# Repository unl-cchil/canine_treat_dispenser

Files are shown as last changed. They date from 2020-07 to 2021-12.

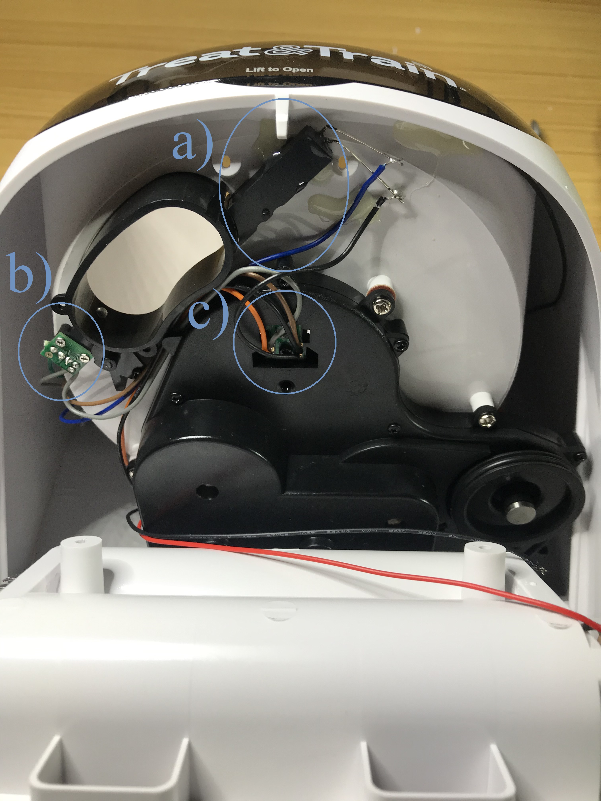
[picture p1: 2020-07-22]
documentation/figures/figure1.jpg

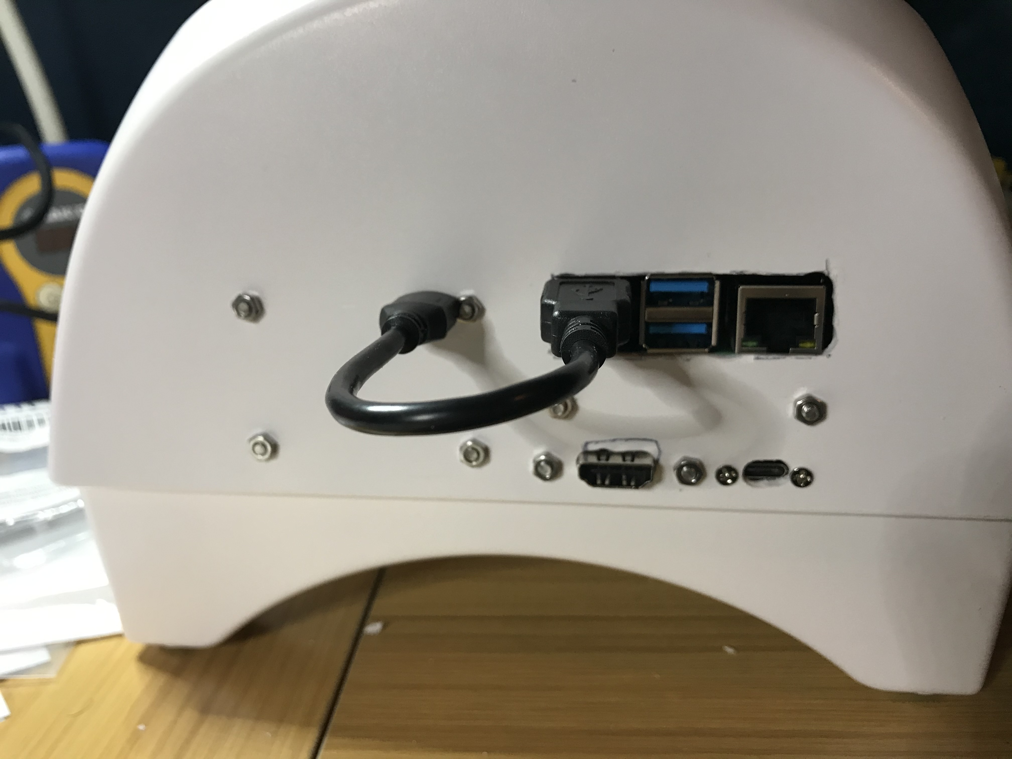
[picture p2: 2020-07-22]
documentation/figures/figure6.jpg

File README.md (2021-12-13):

# Computer-controlled dog treat dispenser

**This project retrofits an existing off-the-shelf dog treat dispenser with new electronics that allow it to be controlled by a computer.**

### Overview

When performing canine operant conditioning studies, the delivery of the reward can be a limiting factor of the study. While there are a few commercially available options for automatically delivering rewards, they generally require manual input, such as using a remote control, in accordance with the experiment script. This means that human reaction times and transmission distances can cause interruptions to the flow of the experiment. The potential for development of non-supervised conditioning studies is limited by this same factor. To remedy this, we retrofitted an off-the-shelf treat dispenser with new electronics that allow it to be remotely controllable as well as act as an experiment computation, data storage, and networking center. We present a fully integrated dispenser driver board with a complementary Raspberry Pi. With rather simple modifications, the commercial treat dispenser can be modified into a computer-controlled dispenser for canine cognition experiments or for other forms of canine training or games.

[Demonstration video](https://www.youtube.com/watch?v=veKvqE5ipu4)

### License

The software and hardware designs are available under a [Creative Commons Attribution-ShareAlike 4.0 International Public License (CC BY-SA 4.0)](https://creativecommons.org/licenses/by-sa/4.0/). You are free to:

* Share — copy and redistribute the material in any medium or format
* Adapt — remix, transform, and build upon the material for any purpose, even commercially.

Under the following terms:

* Attribution — You must give appropriate credit, provide a link to the license, and indicate if changes were made. You may do so in any reasonable manner, but not in any way that suggests the licensor endorses you or your use.
* ShareAlike — If you remix, transform, or build upon the material, you must distribute your contributions under the same license as the original.

### Contact

This project was conducted by the [Canine Cognition and Human Interaction Lab](https://dogcog.unl.edu) and funded by the [National Science Foundation](https://nsf.gov). For questions, please contact the developer Walker Arce (warce@unomaha.edu) or the principal investigator Jeffrey R. Stevens (jeffrey.r.stevens@gmail.com).

### Citation
Arce, W., & Stevens, J. R. (2020). Developing a computer-controlled treat dispenser for canine operant conditioning. _Journal of Open Hardware_, 4(1), 6. https://doi.org/10.5334/joh.27

### Project Mentions
[Hackaday](https://hackaday.com/2020/10/31/using-open-source-to-train-your-dog/)

[Open Neuroscience](https://open-neuroscience.com/post/computer_controlled_dog_treat_dispenser/)

### Dataset Metadata
The following table is necessary for this dataset to be indexed by search
engines such as <a href="https://g.co/datasetsearch">Google Dataset Search</a>.
<div itemscope itemtype="http://schema.org/Dataset">
<table>
<tr>
<th>property</th>
<th>value</th>
</tr>
<tr>
<td>name</td>
<td><code itemprop="name">Computer-controlled dog treat dispenser reliability testing dataset</code></td>
</tr>
<tr>
<td>description</td>
<td><code itemprop="description">The dataset from the paper [Developing a computer-controlled treat dispenser for canine operant conditioning](https://doi.org/10.5334/joh.27). We tested two treat dispensers 100 times each with 10 tests of increasing dispensing targets from 1 to 10 treats. Each row of the data file gives the expected and actual number of treats dispensed for a single trial.</code></td>
</tr>
</tr>
<tr>
<td>url</td>
<td><code itemprop="url">https://github.com/unl-cchil/canine_treat_dispenser</code></td>
</tr>
<tr>
<td>sameAs</td>
<td><code itemprop="sameAs">https://github.com/unl-cchil/canine_treat_dispenser</code></td>
</tr>
<tr>
<td>citation</td>
<td><code itemprop="citation">https://doi.org/10.5334/joh.27</code></td>
</tr>
<tr>
<td>license</td>
<td>
<div itemscope itemtype="http://schema.org/CreativeWork" itemprop="license">
<table>
<tr>
<th>property</th>
<th>value</th>
</tr>
<tr>
<td>name</td>
<td><code itemprop="name">CC BY-SA 4.0</code></td>
</tr>
<tr>
<td>url</td>
<td><code itemprop="url">https://creativecommons.org/licenses/by-sa/4.0/</code></td>
</tr>
</table>
</div>
</td>
</tr>
</table>
</div>

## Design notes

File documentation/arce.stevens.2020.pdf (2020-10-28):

## HARDWARE METAPAPER

# Developing a Computer-Controlled Treat Dispenser for Canine Operant Conditioning

## Walker Arce*

## and Jeffrey R. Stevens†

When performing canine operant conditioning studies, the delivery of the reward can be a limiting factor of the study. While there are a few commercially available options for automatically delivering rewards, they generally require manual input, such as using a remote control, in accordance with the experiment script. This means that human reaction times and transmission distances can cause interruptions to the flow of the experiment. The potential for development of non-supervised conditioning studies is limited by this same factor. To remedy this, we retrofitted an off-the-shelf treat dispenser with new electronics that allow it to be remotely controllable as well as act as an experiment computation, data storage, and networking center. We present a fully integrated dispenser driver board with a complementary Raspberry Pi. With rather simple modifications, the commercial treat dispenser can be modified into a computer-controlled dispenser for canine cognition experiments or for other forms of canine training or games.

Keywords: Canine; computer-controlled dispenser; operant conditioning; retrofitted dispenser
Funding Statement: This research was supported by a National Science Foundation grant to JRS (SES-1658837), including a Research Experiences for Undergraduates (REU) stipend to WA, and by a University of Nebraska-Lincoln Research Council Grant-in-Aid to JRS.

### Metadata Overview

Main design files: https://github.com/unl-cchil/canine_
treat_dispenser. (https://github.com/unl-cchil/canine_treat_dispenser)
Target group: Scientists in canine cognition.
Skills required: Desktop 3D printing, surface mount electronics assembly.
Replication: No builds known to the authors so far.
See section “Build Details” for more detail.

### (1) Overview Introduction

Operant conditioning is a critical tool used to train pet dogs (McKinley and Young 2003). In particular, positive reinforcement involves providing a reward in the presence of a behavior to increase the expression of that behavior (McKinley and Young 2003). Clicker training is a classic example of employing operant conditioning in dogs, where a command is given and, if the dog expresses the correct behavior (or an approximation of that behavior), the dog handler presses the clicker and follows up with a food treat or other reward. These forms of operant conditioning are often used in training obedience and in reducing problem behaviors (Reisner 2016).
Operant conditioning is also used by researchers interested in studying aspects of dog cognition (McKinley and Young 2003). Clicker training, however, is often not ideal for these studies because the clicker and food dispensing must be implemented by a person, which may distract the dog from the cognitive task. For that reason, studies of dog cognition often use automated treat dispensers that are triggered by the researchers, sometimes with remote controls. For example, canine cognition can be tested by dispensing a treat when the animal subject touches a visual indicator on a screen (see demonstration video at https://www.youtube.com/watch?v=veKvqE5ipu4). This allows researchers to present a range of different stimuli to the dogs, record their responses, and reinforce the responses with food treats.
The PetSafe Treat & Train Manners Minder Remote Reward Dog Trainer (PetSafe 2020) is a commercial treat dispenser for training pet dogs at home using operant conditioning techniques. A user can dispense treats using a radio frequency (RF) remote control. The Treat & Train (PetSafe 2020) is a commonly used treat dispenser for canine operant conditioning, and it is generally controlled using its RF remote, dispensing a single treat per button press (Hiby et al. 2004, Yin et al. 2008, Hardin et al. 2015, Protopopova et al. 2016, Majikes 2017, Wallis et al. 2017, Edwards 2019). However, the inconsistencies in the human operating the remote, as well as the remote’s

Arce, W and Stevens, JR. 2020. Developing a Computer-Controlled Treat Dispenser for Canine Operant Conditioning. Journal of Open Hardware, 4(1): 6, pp. 1–10. DOI: https://doi.org/10.5334/joh.27

* Department of Electrical and Computer Engineering, University of Nebraska-Lincoln, US
† Department of Psychology, Center for Brain, Biology and Behavior, University of Nebraska-Lincoln, US
Corresponding author: Jeffrey R. Stevens (jeffrey.r.stevens@gmail.com)

Art. 6, page 2 of 10 | Arce and Stevens: Developing a Computer-Controlled Treat Dispenser for Canine Operant Conditioning

range, can limit the effectiveness of the treat dispenser.
There have been instances of these dispensers being retrofitted to automatically dispense treats, but there have not been any published examples of the method to do so (Wallis et al. 2017). There have, however, been published builds of food-dispensing devices for other species, such as fruit flies (Wayland et al. 2018).
Our aim here is to describe the construction, operation, and reliability of a dispenser that not only is directly controlled by a computer (rather than a remote control) but is a self-contained experimenting system when a Raspberry Pi is integrated into the Treat & Train. To do this, we created a custom-printed circuit board to drive the dispenser. We integrated a Raspberry Pi 4 single-board computer (Raspberry Pi Foundation 2020) and our custom-printed circuit board into the existing Treat & Train (PetSafe 2020) dispenser to create a computer-controlled adaptation of this commonly used device. Our creation allows stimulus generation using common experiment generation software such as PsychoPy (Peirce 2007), controls reward delivery, and performs data collection and transfer in a single, self-contained unit. This paper outlines the methods performed to retrofit the Treat & Train dispenser, the hardware and software designed, and the results of reliability testing in the dispensing of treats. All documentation and firmware are available at https://github.com/unl-cchil/canine_treat_dispenser. (https://github.com/unl-cchil/canine_treat_dispenser)

### Overall Implementation and Design

Treat & Train System
The Treat & Train dispenser consists of a rotating wheel with cutouts that allow treats to fall from the treat storage area to a feeding receptacle. A motor rotates the wheel and a photo interrupter sensor detects whether a treat was dispensed (Figure 1). This means that applying a constant current source to an infrared (IR) transmitter (LED) and an IR receiver and monitoring the output of the receiver will indicate if there is an object blocking the LED. In the case of our system, this would indicate that a treat has been dispensed, which is the output we are trying to detect. Additionally, there is a photo interrupter in the base of the dispensing wheel that can detect the movement of the wheel.
To power the IR LED, we inserted a current-limiting resistor in series with the LED power supply. On the negative end we wanted to monitor the output voltage, which should be proportional to the amount of IR light interacting with it. To do this, we placed a resistor divider of sufficiently high resistance to measure the output voltage. This allows the circuit to act as a voltmeter and gives us sufficient resolution to detect treats crossing the IR beam. The Treat & Train has a brushed DC motor on-board that drives a gear and pulley system to the main dispensing wheel. The stock dispenser drives this motor at 6 VDC in one direction. For our purposes, we allowed more flexibility by

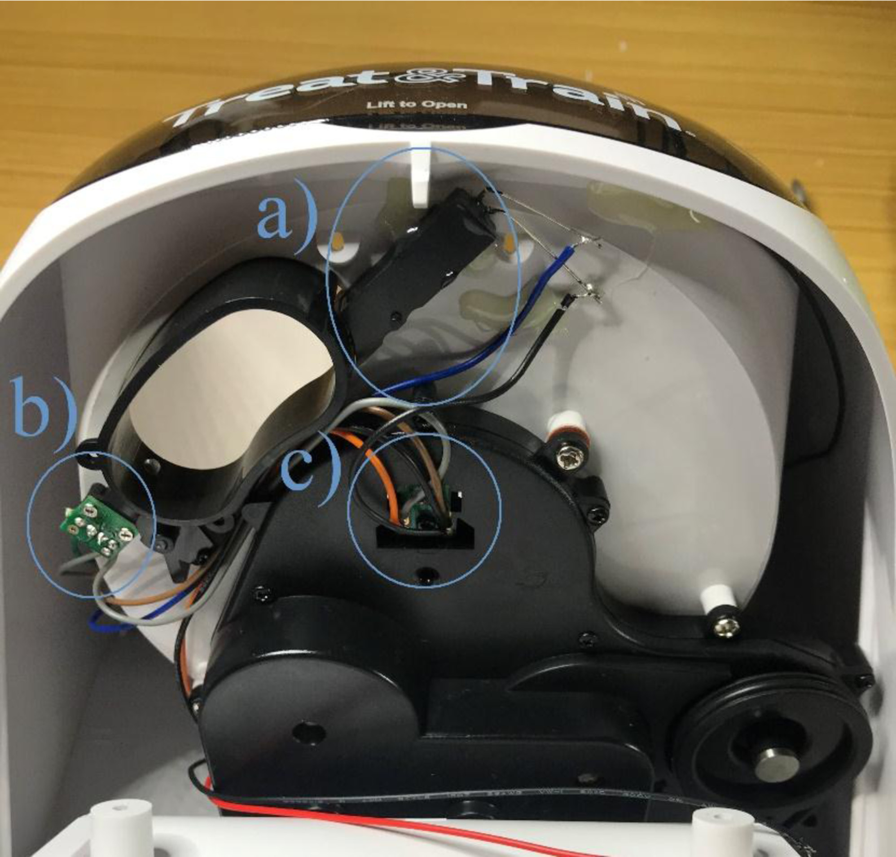
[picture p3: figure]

Figure 1: Location of the two IR transmitter-receiver pairs, where (a) is the treat IR receiver, (b) is the treat IR LED—so
(a) and (b) constitute a single photo interrupter—and (c) is the wheel photo interrupter, with both parts integrated into a single package.

Arce and Stevens: Developing a Computer-Controlled Treat Dispenser for Canine Operant Conditioning | Art. 6, page 3 of 10

using a motor driver chip to drive the motor and control
its speed. To drive a 6 VDC motor from a USB power supply, which is set to 5 VDC, we needed to boost the voltage. To allow some excess capacity/voltage for future implementations, we designed a boost regulator with an output voltage of 12 VDC.

Hardware Development
We developed a simple driver board with a USB interface, microcontroller, power stage, motor interface, and an interface for the Treat & Train sensors. We used a microcontroller to drive these circuits, an ARM Cortex-M0+, which is supported by the Arduino IDE for easy programmability and customization. This system was then paired with a Raspberry Pi 4 to create a self-contained dispenser. Additionally, we combined this system with a television display and a USB infrared touchscreen device that is used as mouse input. The result is a complete operant system in which stimuli are presented on the television display, responses are recorded by the touchscreen, and treats are automatically dispensed based on the responses (see demonstration video at https://www.youtube.com/watch?v=veKvqE5ipu4). (https://www.youtube.com/watch?v=veKvqE5ipu4) The connection diagram for this is shown in Figure 2.

Next, we designed the interfaces to the Treat & Train main board, which had all of its internal connections severed to be interfaced to our circuits. The first circuit is the digital interface for the RF remote ‘click’ signal that dispenses treats. This is triggered by connecting the positive motor output of the Treat & Train main board to a transistor circuit that would energize when the main board tries to drive the motor. This retains RF remote control functionality. The second circuit is the analog voltage sensing resistor divider, for which we used 1 MΩ resistors to keep the current drawn low. These are shown in Figure 3.
For the custom board, we used an ARM Cortex-M0+ microcontroller (ATSAMD21E from Microchip), with a TB6612 motor driver (Figure 4). The USB voltage was regulated to 3.3 VDC using an AP2112k low dropout regulator and the 12 VDC for the motor was generated using an LMR6201 1.6 MHz step-up converter with a 1.4 A switch. Finally, the right-angle USB connector was mounted such that it would be exposed out of the back wall of the Treat & Train.
This board was designed to work with the “Sparkfun Qwiic Micro” bootloader (Microsoft 2019) that is available through the Boards Manager in the Arduino IDE. Reference this firmware when determining what the

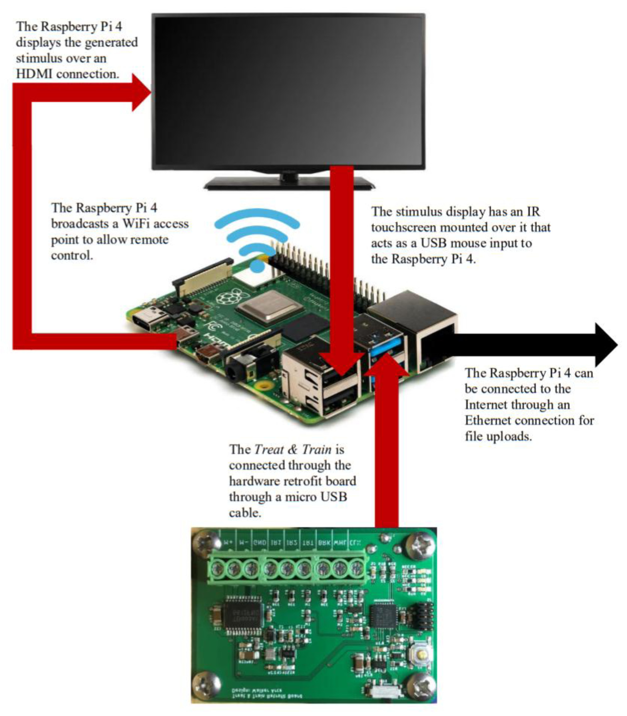
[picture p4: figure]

Figure 2: Connection diagram for the developed hardware.

Art. 6, page 4 of 10 | Arce and Stevens: Developing a Computer-Controlled Treat Dispenser for Canine Operant Conditioning

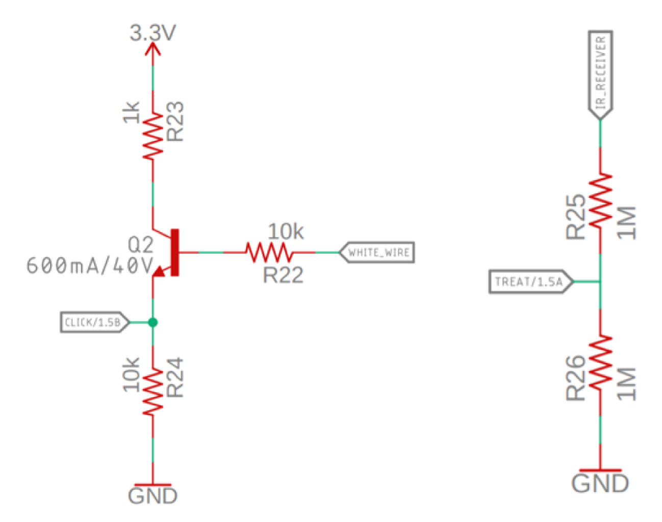
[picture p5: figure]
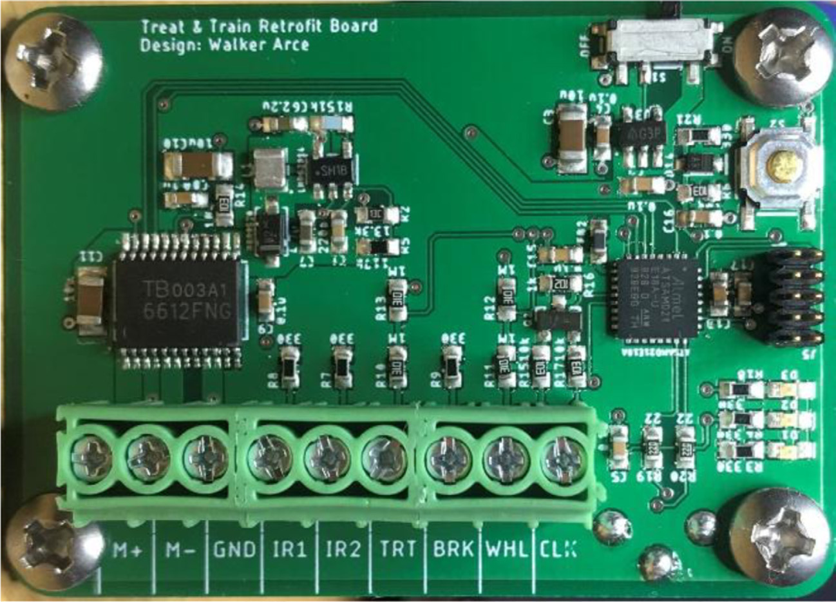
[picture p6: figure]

Arduino pin names refer to if using this firmware with another processor. The pins that are broken out on the screw terminals are shown in Table 1 and are valid for firmware version 0.4.
The internal connections from the microcontroller to the motor driver are specified in Table 2.

Software Development
Our implementation will have two sets of software: one set that runs on the microcontroller and another that runs on a host computer, in this case the Raspberry Pi. We composed the first set in the Arduino IDE 1.8.12 (Arduino 2020) using an open-source bootloader and the second using Python (Python Software Foundation 2019), which allows for cross-platform compatibility and testing.
The firmware for the current implementations is at version 0.4 and was designed using the Arduino IDE 1.8.12 (Arduino 2020). The firmware running on the custom-printed circuit board operates using a defined USB protocol driven by byte codes. This can be easily expanded upon by adding cases to the switch statement for the command byte (Table 3). A response of 0x00 indicates the command successfully executed and a response of 0x01 indicates the command failed. Commands are processed in the order they are received.

Figure 3: (Left) Transistor to detect the RF remote being activated, (Right) resistor divider circuit to read the IR receiver output voltage. Note: “WHITE WIRE” is the hardware connection to the RF receiver; “CLICK” is the output signal for the RF receiver; “TREAT” is the voltage reading from the output of the IR receiver.

Figure 4: Custom printed circuit board.

Arce and Stevens: Developing a Computer-Controlled Treat Dispenser for Canine Operant Conditioning | Art. 6, page 5 of 10

There are a few pre-defined commands for this version of the firmware, one of which is not accessible through USB input (Table 4).
On the Pi, a Python class was implemented to send the above commands over a USB serial link to the driver board. This class was used with PsychoPy in the experiment script.

Dispenser Development
To run entire experimental setups, perform the visualization of input stimulus, control stimulus devices, and log generated data, we integrated a Raspberry Pi 4 (Raspberry Pi Foundation 2020) single-board computer running the default Raspberry Pi OS (Raspberry Pi Foundation 2020). This allowed us to achieve three goals:
1 | Wireless Access Point
| – The Raspberry Pi 4 can host its own WiFi access
| point, which allows the experimenter to connect
| to the Pi and run experiments, download results,
| and interact with the main system.
2 | Decoupled Interfaces
| – The experimenter’s screen and the screen used
| by the canine are separate and require no extra
| hardware to achieve. By connecting to the Pi us-
| ing SSH (Secure Shell), the command line can

be exposed to run the experiments. The canine screen can be connected to the HDMI0 of the Pi and the SSH session can be started over a wireless connection.
3 | Simple Setup
| – The system is expected to be easy to setup and
| maintain. We can use robust packages such as pi-
| ap (Houlahan 2019) and SD card backups to eas-
| ily restore the dispenser and get new dispensers
| up and running.

Achieving the above three criteria allows for a launching point towards more complex and integrated solutions for automated reward delivery and data logging.
The final dispenser with the new electronics and functionality had its connectors exposed on the back wall of the dispenser. The connections include the USB connector to the retrofitted control board, the Raspberry Pi 4 USB connectors, an HDMI port, Ethernet jack, and the USB-C power supply input port. This allows the Raspberry Pi 4 to display stimuli on a screen connected to the HDMI port and accept mouse inputs from an IR touchscreen adapter through on of the Pi USB ports. The Pi can also be network connected through the Ethernet jack. A short USB cable from the Pi provides power and serial communications

Table 1: Custom board pin descriptions and functions, applicable to firmware version 0.4.

Pin Name Arduino Pin Function Description
M+ | N/A | Output | Connected to positive motor pin
M- | N/A | Output | Connected to negative motor pin
GND | N/A | Input | Common ground pin
IR1 | N/A | Output | 3.3V power supply for IR LEDs, current limited to 5mA
IR2 | N/A | Output | 3.3V power supply for IR LEDs, current limited to 5mA
TRT | A1 | Input | IR receiver sensor from treat sensor
BRK | N/A | Output | 3.3V power supply for photointerrupter sensors, current limited to 1mA
WHL | A3 | Input | IR receiver sensor output from wheel sensor
CLK | D8 | Input | RF remote input for ‘Dispense’ button

Table 2: Arduino pin names and descriptions.

Pin Name Arduino Pin Description
AIN1 | D7 | First input for motor driver, invert from other input to drive motor in one direction or the other.
AIN2 | D6 | Second input for motor driver, invert from other input to drive motor in one direction or the other.
PWMA | D3 | PWM input that controls the speed of the motor

Table 3: USB protocol byte descriptions.

| Name | Value | Function
Start Byte | 67 (Dec), 0x43, ‘C’ Signals the system to start listening for input
Command Byte 1 byte | Command defined below
| Data Byte | 1 byte | Defined based on commands
End Byte | 69 (Dec), 0x45, ‘E’ Signals the end of the current command

Art. 6, page 6 of 10 | Arce and Stevens: Developing a Computer-Controlled Treat Dispenser for Canine Operant Conditioning

to the driver board. This USB cable can be removed from the Pi, and the dispenser can be connected directly to a standard PC—bypassing the Raspberry Pi—to operate the retrofitted dispenser. This is shown in Figure 5.
The dispenser, when turned on, creates a WiFi access point called “operant-canine-xx”, with “xx” being the dispenser number, i.e. “01” with a local address of
pi@192.168.0.1 and the password raspberry,
which are the default values in the pi-ap configuration. This can be modified in the pi-ap software. By connecting to this AP, the Raspberry Pi can be accessed through SSH using a program such as PuTTY (Tatham 2020).
To use the RF remote to trigger the system, the Treat & Train main board must first be turned on before powering on the retrofitted board. If the Treat & Train is turned on after the retrofitted board, the ‘CLK’ signal will go high, as it is controlled through a transistor that is not turned off when the board is first powered on. Do not use anything other than a computer USB port for powering the system. The retrofitted board does not power the Treat & Train main board, so it will still require four D cell batteries to operate with backwards compatibility. This should be fixed in the next revision and the RF receiver should be powered by the custom printed circuit board.

### (2) Quality Control Safety

Operators of this dispenser should be aware of four hazards:

- Finger pinches.
- Electric shock.
- Burns when assembling electronics.
- Damage to Treat & Train.

Finger Pinches
The dispenser wheel turns continuously from a DC motor to dispense treats through an eyelet that, if not careful, can cause the user’s finger to be pinched when trying to fix a jam.

Electric Shock
The powering of electronics using an external power source, such as when testing a newly developed circuit, can cause electric shocks if not careful. Work tables should be placed where there is no risk of splashing water. All cables used to connect sensors and power should be inspected for damage and replaced if necessary.

Burns during Assembly
The assembly of the described electronics includes the use of soldering irons and hot air rework tools. These tools use high temperatures to melt solder and pose a risk of burning when used improperly. Ensure that the user’s manuals are read and adhered to when using new tools.

Damage to Treat & Train
When retrofitting an off-the-shelf device, there is always a risk of damaging or destroying the on-board electronics. Before applying power to any on-board sensors, double check your power supply and connections to prevent short circuits and over-voltage/over-current situations.

### General Testing

Considering one line of canine behavior and psychology research includes the design of numerical preference studies (Ward 2007, Baker 2012, Miletto Petrazzini et al. 2020), we tested the dispenser’s accuracy of dispensing treats. This gives benchmarks that allow for future work that may be needed to meet specific performance deficits that exist in the current setup and for the dispenser to be adapted to new types of studies.
For this testing, we wanted to measure the failure rate of the dispensing commands, meaning the amount over or under that it dispenses from the target amount. To do this, we performed a total of 100 tests split into 10 tests of increasing dispensing targets from 1 to 10 treats, in steps of one treat. These tests were performed using two of the described dispensers, which were filled up to the “1 cup” line with Pet Botanics Training Reward treats, which are cylindrical treats that fit through the larger dispenser wheel. Reliability data are available at https://github.com/unl-cchil/canine_treat_dispenser. (https://github.com/unl-cchil/canine_treat_dispenser)
The results for this testing are shown in Tables 5 and 6. We tracked the mean number of treats dispensed for each dispenser tested (columns Actual One and Two), the number of treats dispensed that were over or under the expected number in each set of tests (columns Errors One

Table 4: USB commands that follow Table 3 protocol.

Command | Command Byte Data | Function
Dispense | ‘D’ | ‘0’–’9’ Command to dispense up to 9 treats.
Print | ‘P’ | ‘0’ | Prints current value of sensors, data field is set to zero in ASCII (‘0’).
Update RF | ‘B’ | ‘0’–’9’ Updates the number of treats that will be dispensed when using the RF remote.
Dispense | ‘A’ | 0–255 Command to dispense up to 255 treats.
Motor Update ‘M’ | 0–255 Updates the motor speed used when operating the dispenser in any mode.
| | | Default: 127
Wheel Test | ‘F’ | ‘0’ | Performs the wheel test routine to verify operation of the firmware and sensors.
RF Dispense | N/A | N/A | By clicking the ‘Dispense’ button on the RF remote, the system will dispense the defined number of treats. Default: 1 treat

Arce and Stevens: Developing a Computer-Controlled Treat Dispenser for Canine Operant Conditioning | Art. 6, page 7 of 10

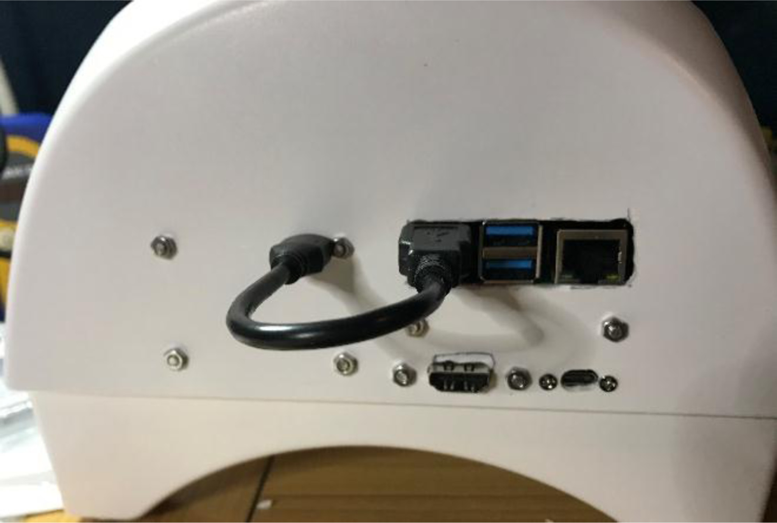
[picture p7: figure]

and Two), the mean number of treats dispensed averaged across the two dispensers (column Mean Actual), and the mean number of failures between the two dispensers (Mean Error).
Each dispensing command has a potential error rate of 32% in the first dispenser and 22% in the second dispenser. This means that over- or under-dispensing occurs roughly every third and fourth event, respectively.

### (3) Application Use Case(s)

The modified Treat & Train was designed to be used in canine cognition studies and be controlled by a script to perform the reward dispensing in response to input from the canine subject. This described tools can also reasonably act as a platform for new dispenser development, which can be specifically designed for canine cognition research, such as precise dispensers.

Figure 5: Peripheral interface for the dispenser.

Table 6: Results of the reliability testing.

Dispense | Actual One Actual Two Errors One Errors Two Mean Actual Mean Error
1 | 1.10 | 1.00 | 1 | 0 | 1.05 | 0.50
2 | 2.40 | 2.20 | 4 | 2 | 2.30 | 3.00
3 | 3.40 | 3.30 | 4 | 3 | 3.35 | 3.50
4 | 4.10 | 4.00 | 1 | 0 | 4.05 | 0.50
5 | 5.20 | 5.30 | 2 | 3 | 5.25 | 2.50
6 | 6.40 | 6.50 | 4 | 5 | 6.45 | 4.50
7 | 7.60 | 7.10 | 6 | 1 | 7.35 | 3.50
8 | 8.50 | 8.60 | 4 | 4 | 8.55 | 4.00
9 | 9.50 | 9.20 | 4 | 2 | 9.35 | 3.00
10 | 10.00 | 10.20 | 2 | 2 | 10.10 | 2.00
Mean Error | | | 32.0% | 22.0% | | 27.0%

Table 5: Results of the treat dispensing trials.

Total Treats
Dispensed

Correct Number
Dispensed

Over-Dispensing Under-Dispensing

First Dispenser | 100 | 68 | 31 | 1
Second Dispenser | 100 | 78 | 22 | 0

Art. 6, page 8 of 10 | Arce and Stevens: Developing a Computer-Controlled Treat Dispenser for Canine Operant Conditioning

Further, this may be used by dog owners who are training their dogs for particular tasks or who would like to
develop games for their dogs to play. Existing commercial dispensers such as PupPod (PupPod 2020) allow for inputs from embedded sensors in toys. But they do not connect to touchscreens, which could provide rich possibilities for games. Our dispenser allows a wider range of potential stimuli to be presented to and responses to be recorded from dogs to trigger a reward.
Since the Raspberry Pi 4 has an on-board Bluetooth modem, this allows for integration of other custom devices such as inertial measurement units (IMUs), which measure its own movement in terms of acceleration in the X, Y, and Z axes, to allow a canine’s position and movement to control treat dispensing (Protopopova et al. 2016, Majikes 2017). Additionally, the sound output of the Pi can allow for sound triggers in the operant conditioning protocol (Protopopova et al. 2016, Edwards 2019).

### Reuse Potential and Adaptability

With the included Raspberry Pi 4, custom sensors can be easily integrated through Python scripting to trigger the dispensing command. The developed Python class and custom hardware allow for control of other dispensers, such as for bird or rat pellets. Common off-the-shelf dispensers use a single motor to dispense sequential treats, in a similar fashion as the Treat & Train; due to this the presented hardware would work on those systems.

### (4) Build Details Availability of Materials and Methods

Building the custom hardware requires the use of a soldering iron, hot air rework gun, reflow oven, precise tweezers, and a vise. All the parts for this part of the build are available from DigiKey and a PCB manufacturer.
The retrofitting operation requires a 3D printed Raspberry Pi mount, a Dremel for exposing ports on the Treat & Train, and various M3 screws. Additionally, the extra parts, such as HDMI cables and ports, for the Raspberry Pi 4 are available from Amazon.

### Ease of Build

The parts used in the build are readily available from online vendors such as Adafruit and DigiKey. The custom version requires the operation of more advanced tools such as a hot air gun or reflow oven, pick and place or precise tweezers, and solder paste and flux. We estimate the build can be performed in around eight hours with sufficient planning and experience from start to finish for the DIY version.

### Operating Software and Peripherals

For the custom hardware, Arduino IDE 1.8.12 was used as the development environment. For the Raspberry Pi 4, the Raspberry Pi OS was used as well as pyserial (version 3.4), PsychoPy (version 3.2.4), and pi-ap (version 1.10.02).

### Dependencies

This build requires the use of pi-ap (Houlahan 2019), Raspberry Pi OS (Raspberry Pi Foundation 2020), and

Arduino IDE (Arduino 2020). The driving software to send commands over the USB port is written in Python 3.7.6 (Python Software Foundation 2019).

### Hardware Documentation and File Location

Name: GitHub
Persistent identifier: https://github.com/unl-cchil/canine_treat_dispenser (https://github.com/unl-cchil/canine_treat_dispenser)
Licence: Creative Commons CC-BY-SA, 4.0 Publisher: Jeffrey R. Stevens
Date published: 29/07/2020
Software is stored together with the hardware files, in the same repository.
Licence: Creative Commons CC-BY-SA, 4.0
Date published: 29/07/2020

### (5) Discussion Conclusions

This study presented a method by which a common, offthe-shelf, canine treat dispenser can be modified to conduct operant conditioning studies using a computer interface. Using the presented version, the common Arduino platform was used to interface to the onboard photo interrupters and control the dispensing motor, achieving the same functionality as the original dispenser but controlled by a computer. This computer, a Raspberry Pi 4, was integrated to the new hardware to run a Linux distribution and operate the generation of stimulus through PsychoPy (Peirce 2007). In adding this central computing platform, all results from the experiments can be centrally stored and easily accessed for future processing and reporting.
By making this dispenser DIY and open-source, researchers may expand on the work and include new trigger methods ranging from sound to ultrasonic distance sensing. By having a single-board computer housed within the dispenser, experiment control software can be generated and run by using the tested and supported PsychoPy Python package (Peirce 2007). Additionally, this setup allows for cross-platform development, meaning that any software already generated using the PsychoPy package is supported. The inclusion of the Raspberry Pi 4 also makes the entire setup mobile, so experiments can be conducted outside of the laboratory.
The demonstrated computer-controlled dispenser can be readily used and assembled with minimal skill and can act as a jumping off point for automated canine operant conditioning studies. Since automated reward dispenser are difficult to build from scratch, our proposed modifications of the Treat & Train would allow for researchers to integrate an automated dispenser into their studies (Hardin et al. 2015, Protopopova et al. 2016, Majikes 2017, Wallis et al. 2017, Robinson et al. 2020). Additionally, since the use of positive reinforcement training has been shown to indicate an increased level of obedience, our dispenser can be used in at-home situations for canine training exercises (Hiby et al. 2004).
The average error rate between the two dispensers is 27%, which is an error every fourth dispensing command. These errors often happen when two treats stack in the

Arce and Stevens: Developing a Computer-Controlled Treat Dispenser for Canine Operant Conditioning | Art. 6, page 9 of 10

output hole and, when it dispenses, both fall through,
leading to dispensing one extra treat. If, for instance,
a circular or thicker treat were used, this issue could be mitigated. Alternatively, modifying the dispensing wheel to limit the number of treats grabbed could also help. As for situations where the treat would jam the movement of the wheel, the force of the turning wheel would cut the treat in half, as the treats used in testing were pliable enough to allow for this. This resolved the issue when it presented itself, but this may not be the case for all treat types.
For studies in which precise treat dispensing is not required, our work allows researchers to relatively inexpensively adapt an off-the-shelf product into a treat dispenser that can be controlled either by a personal computer or a Raspberry Pi, thus facilitating operant conditioning studies in dogs.

### Future Work

Our results indicate that the developed dispenser is most likely not suitable for precise dispensing experiments, such as numerical preference experiments. Due to this, our focus will be to prove out the developed dispenser for canine cognition studies and stress test the current design. Additionally, to make the developed printed circuit board more easily integrated, it would be beneficial to adapt it into a Raspberry Pi HAT (Hardware Attached on Top), in which the board is directly attached to the Raspberry Pi.

### Additional File

The additional file for this article can be found as follows:

- Data file. CSV file of reliability testing data. DOI: https://doi.org/10.5334/joh.27.s1

### Acknowledgements

We thank Harold Tay for comments on this manuscript.

### Competing Interests

The authors have no competing interests to declare.

### Author Contributions

Design, assembly, testing, paper writing and editing, Walker Arce.
Oversight, funding, paper writing and editing, Jeffrey R. Stevens.

### References

Arduino. (2020). Arduino. Available at: https://www.arduino.cc/.
Baker, J. M., Morath, J., Rodzon, K. S. and Jordan, K. E. (2012). A shared system of representation governing quantity discrimination in canids. Frontiers in Psychology, 3: 387. DOI: https://doi.org/10.3389/fpsyg.2012.00387 (https://doi.org/10.3389/fpsyg.2012.00387)
Edwards, T. L. (2019). Automated canine scent-detection apparatus: technical description and training outcomes. Chemical Senses, 44(7): 449–455. DOI: https://doi.org/10.1093/chemse/bjz039

Hardin, D. S., Anderson, W. and Cattet, J. (2015). Dogs can be successfully trained to alert to hypoglycemia samples from patients with type 1 diabetes. Diabetes Therapy, 6(4): 509–517. DOI: https://doi.org/10.1007/s13300-015-0135-x (https://doi.org/10.1007/s13300-015-0135-x)
Hiby, E. F., Rooney, N. J. and Bradshaw, J. W. S. (2004). Dog training methods: their use, effectiveness and interaction with behaviour and welfare. Animal Welfare, 13(1): 63–70.
Houlahan, T. (2019). pi-ap. Available at: https://github.com/f1linux/pi-ap. (https://github.com/f1linux/pi-ap)
Majikes, J. J. (2017). Computational and design techniques for a semi-autonomous computerized dog-training system with timing and accuracy performance comparable to a professional dog trainer. (Unpublished doctoral dissertation, North Carolina State University). McKinley, S. and Young, R. J. (2003). The efficacy of the model–rival method when compared with operant conditioning for training domestic dogs to perform a retrieval–selection task. Applied Animal Behaviour Science, 81(4): 357–365. DOI: https://doi.org/10.1016/S0168-1591(02)00277-0 (https://doi.org/10.1016/S0168-1591(02)00277-0)
Miletto Petrazzini, M. E., Mantese, F., and Prato-Previde, E. (2020). Food quantity discrimination in puppies (Canis lupus familiaris). Animal Cognition, 23: 703–710. DOI: https://doi.org/10.1007/s10071-020-01378-z (https://doi.org/10.1007/s10071-020-01378-z)
Microsoft. (2019). uf2-samdx1. Available at: https://github.com/microsoft/uf2-samdx1.
Peirce, J. W. (2007). PsychoPy—Psychophysics software in Python. Journal of Neuroscience Methods, 162(1–2): 8–13. DOI: https://doi.org/10.3758/s13428-018-01193-y (https://doi.org/10.3758/s13428-018-01193-y)
PetSafe. (2020). Treat & Train™ Remote Reward Dog Trainer. Available at: https://intl.petsafe.net/en-gb/support/treat-train-remote-reward-dog-trainer. (https://intl.petsafe.net/en-gb/support/treat-train-remote-reward-dog-trainer) Protopopova, A., Kisten, D. and Wynne, C. (2016). Evaluating a humane alternative to the bark collar: Automated differential reinforcement of not barking in a home‐alone setting. Journal of Applied Behavior Analysis, 49(4): 735–744. DOI: https://doi.org/10.1002/jaba.334 (https://doi.org/10.1002/jaba.334)
PudPod. (2020). Puzzle Toy for Dogs. PupPod. Available at: https://puppod.com/.
Python Software Foundation. (2019). Python Release Python 3.7.6. Python.org. Available at: https://www.python.org/downloads/release/python-376/. Raspberry Pi Foundation. (2020). Teach, Learn, and Make with Raspberry Pi – Raspberry Pi. Available at: https://www.raspberrypi.org/.
Reisner, I. (2016). The learning dog: A discussion of training methods. In J. Serpell (Ed.), The Domestic Dog: Its Evolution, Behavior and Interactions with People, 2: 211–226. Cambridge University Press.
Robinson, C., Brulé, E., Jackson, J., Torjussen, A., Kybett, J. and Appshaw, T. (2020). Tricks and treats: Designing technology to support mobility assistance dogs. In: Proceedings of the 2020 CHI Conference on Human Factors in Computing Systems, Honolulu, HI, USA on 25–30 April 2020, pp. 1–14.

Art. 6, page 10 of 10 | Arce and Stevens: Developing a Computer-Controlled Treat Dispenser for Canine Operant Conditioning

Tatham, S. (2020). Download PuTTY: latest release (0.74).
Available at: https://www.chiark.greenend.org.
uk/~sgtatham/putty/latest.html. (https://www.chiark.greenend.org.uk/~sgtatham/putty/latest.html)
Wallis, L. J., Range, F., Kubinyi, E., Chapagain, D., Serra, J. and Huber, L. (2017). Utilising dogcomputer interactions to provide mental stimulation in dogs especially during ageing. In: Proceedings of the Fourth International Conference on Animal-Computer Interaction, New York, NY, USA on November 2017, pp. 1–12. DOI: https://doi.org/10.1145/3313831.3376188 (https://doi.org/10.1145/3313831.3376188)
Ward, C. and Smuts, B. B. (2007). Quantity-based judgments in the domestic dog (Canis lupus familiaris).

Animal Cognition, 10(1): 71–80. DOI: https://doi.org/10.1007/s10071-006-0042-7 (https://doi.org/10.1007/s10071-006-0042-7)
Wayland, M. and Landgraf, M. (2018). A Cartesian coordinate robot for dispensing fruit fly food. Journal of Open Hardware, 2(1): 3. DOI: https://doi.org/10.5334/joh.9 (https://doi.org/10.5334/joh.9)
Yin, S., Fernandez, E. J., Pagan, S., Richardson, S. L. and Snyder, G. (2008). Efficacy of a remote-controlled, positive-reinforcement, dog-training system for modifying problem behaviors exhibited when people arrive at the door. Applied Animal Behaviour Science, 113(1–3): 123–138. DOI: https://doi.org/10.1016/j.applanim.2007.11.001 (https://doi.org/10.1016/j.applanim.2007.11.001)

How to cite this article: Arce, W and Stevens, JR. 2020. Developing a Computer-Controlled Treat Dispenser for Canine Operant Conditioning. Journal of Open Hardware, 4(1): 6, pp. 1–10. DOI: https://doi.org/10.5334/joh.27
Published: 28 October 2020
Copyright: © 2020 The Author(s). This is an open-access article distributed under the terms of the Creative Commons Attribution 4.0 International License (CC-BY 4.0), which permits unrestricted use, distribution, and reproduction in any medium, provided the original author and source are credited. See http://creativecommons.org/licenses/by/4.0/.
OPEN ACCESS Journal of Open Hardware is a peer-reviewed open access journal published by Ubiquity Press.

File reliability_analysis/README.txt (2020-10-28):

ReadMe file
Created on 2020-09-29 by Jeffrey R. Stevens (jeffrey.r.stevens@gmail.com)

**********************************************************
If you use the data, please cite the following:
Arce, W., & Stevens, J. R. (2020). Developing a computer-controlled treat dispenser for canine operant conditioning. Journal of Open Hardware, 4(1), 6. https://doi.org/10.5334/joh.27
**********************************************************

Summary: We tested two treat dispensers 100 times each with 10 tests of increasing dispensing targets from 1 to 10 treats. Each row of the data file gives the expected and actual number of treats dispensed for a single trial.

License:
All materials presented here are released under the Creative Commons Attribution 4.0 International Public License (CC BY 4.0). You are free to:
    Share — copy and redistribute the material in any medium or format
    Adapt — remix, transform, and build upon the material for any purpose, even commercially.
Under the following terms:
    Attribution — You must give appropriate credit, provide a link to the license, and indicate if changes were made. You may do so in any reasonable manner, but not in any way that suggests the licensor endorses you or your use.
    No additional restrictions — You may not apply legal terms or technological measures that legally restrict others from doing anything the license permits.

Data files:
arce_stevens_2020_data.csv
 dispenser - dispenser number (1 or 2)
 trial - trial number
 expected - expected number of treats dispensed
 actual - actual number of treats dispensed

R code:
 arce_stevens_2020_rcode.R - code for running computations

Instructions to reproduce results:
 To reproduce these results, open arce_stevens_2020_rcode.R and ensure that all packages mentioned at the top of the script are installed.  Once all packages are installed, run the script in R using "source("arce_stevens_2020_rcode.R")".

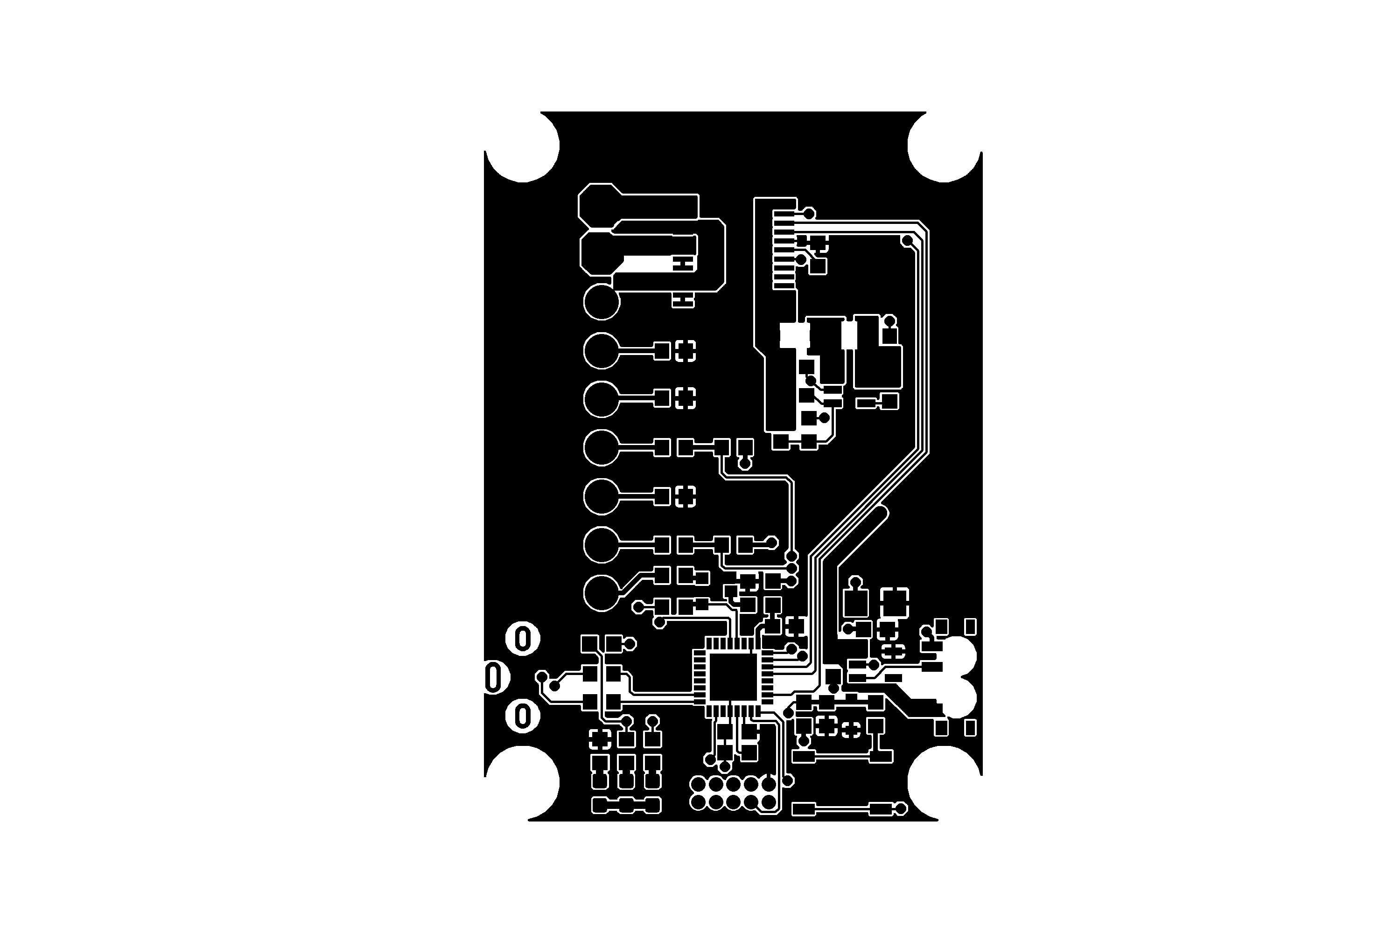
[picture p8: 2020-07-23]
hardware/retrofit controller/pcb files/renders/TopCopper.png

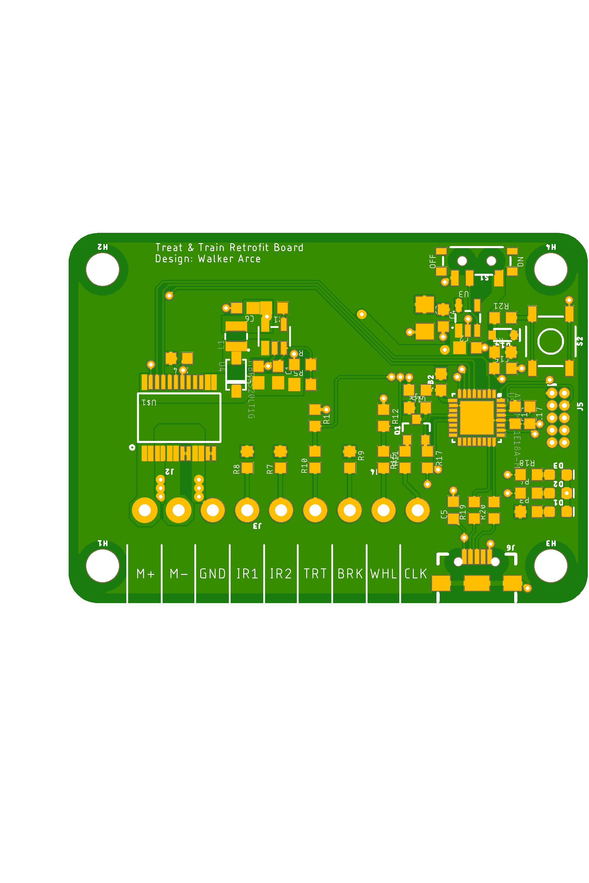
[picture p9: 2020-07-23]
hardware/retrofit controller/pcb files/renders/BoardTopV1.0.png

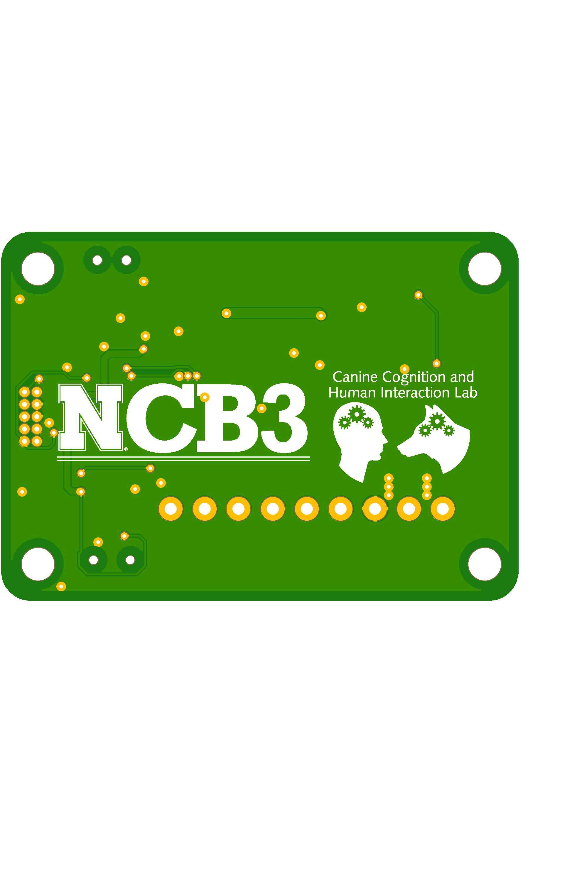
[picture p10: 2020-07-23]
hardware/retrofit controller/pcb files/renders/BoardBottomV1.0.png

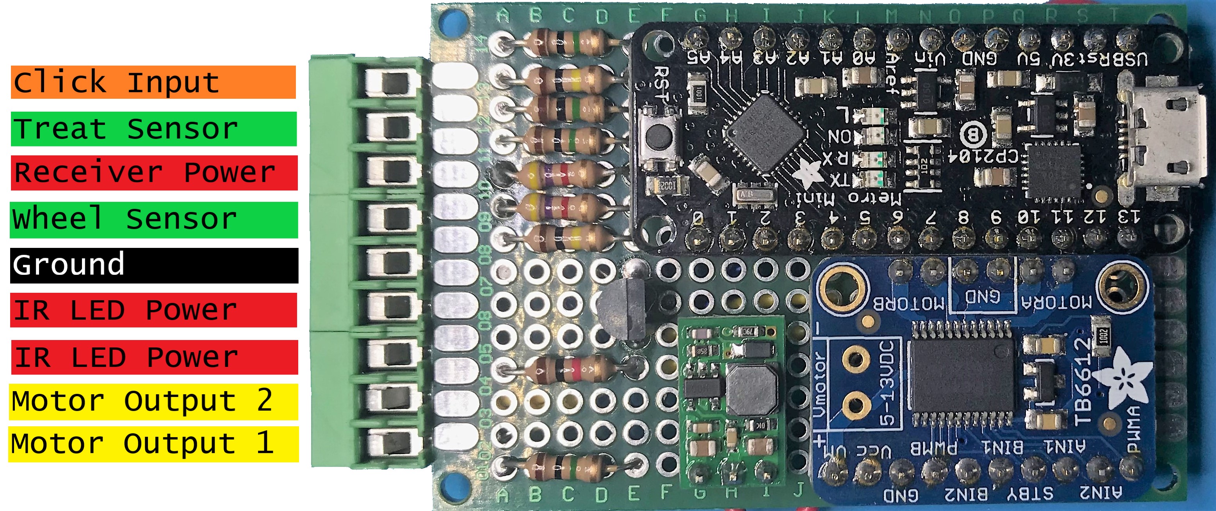
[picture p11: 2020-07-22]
documentation/figures/figure4.jpg

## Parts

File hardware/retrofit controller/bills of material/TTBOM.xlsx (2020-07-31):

Bill of Materials - Treat&Train Retrofit Board |  |  |  |  |  |  | Bill of Materials - Treat&Train Retrofit Board |  |  |  | Bill of Materials - Treat&Train DIY Version
Part | Description | Supplier | Part Number | Quantity | Price | Final Price | Part | Supplier | Quantity | Price | Part | Description | Supplier | Part Number | Quantity | Price | Final Price
ATSAMD21E | Microcontroller | DigiKey | ATSAMD21E18A-MUTCT-ND‎ | 1 | $2.92 | $2.92 | Raspberry Pi 4 | Sparkfun | 1 | $59.95 | Metro Mini 328 | Microcontroller | DigiKey | 1528-1374-ND | 1 | $12.50 | $12.50
TB6612FNG | Motor Driver | DigiKey | TB6612FNGC8ELCT-ND | 1 | $1.95 | $1.95 | 16 GB SD Card | Amazon | 1 | $6.99 | TB6612 Breakout | Motor Driver | DigiKey | 1528-1212-ND | 1 | $4.95 | $4.95
LMR6201 | 12V Boost | DigiKey | LMR62014XMFE/NOPBCT-ND | 1 | $1.64 | $1.64 | Power Supply | Sparkfun | 1 | $8.00 | 12V Boost Module | Step Up Module | Pololu | 2117 | 1 | $3.95 | $3.95
AP2112K | 3.3V LDO | DigiKey | AP2112K-3.3TRG1DICT-ND | 1 | $0.49 | $0.49 | USB C Panel Mount Cord | Amazon | 1 | $8.99 | Screw Terminal | Sensor Connectors | DigiKey | ED10562-ND | 3 | $1.03 | $3.09
Vertical USB | USB Connector | DigiKey | ‎WM9734CT-ND‎ | 1 | $1.11 | $1.11 | HDMI Panel Mount | Amazon | 1 | $1.59 | 2N3904 | Click Signal Transistor | DigiKey | 2N3904FS-ND | 1 | $0.20 | $0.20
Screw Terminal | Sensor Connectors | DigiKey | ED10562-ND | 3 | $1.03 | $3.09 | Micro HDMI to HDMI Cord | Amazon | 1 | $5.41 | 1M Res THT | Voltage Sense Resistors | DigiKey | CF18JT1M00CT-ND | 4 | $0.10 | $0.40
Debug Header | Programming Header | DigiKey | 609-3712-ND | 1 | $0.69 | $0.69 | Micro USB to USB A Cord | Sparkfun | 1 | $1.95 | 10k Res THT | Pull up and current | DigiKey | CF14JT10K0CT-ND | 2 | $0.10 | $0.20
SPST Switch | Reset Button | DigiKey | CKN12223-1-ND | 1 | $0.10 | $0.10 |  |  |  |  | 4.7k Res THT | Transistor bias | DigiKey | CF14JT4K70CT-ND | 2 | $0.10 | $0.20
SPDT Switch | Power Switch | DigiKey | 401-2016-6-ND | 1 | $0.91 | $0.91 |  |  |  | $92.88 | 1k Res THT | Current setting | DigiKey | CF14JT1K00CT-ND | 1 | $0.10 | $0.10
Stand Off | Board Mounting | DigiKey | 36-24434-ND | 4 | $0.42 | $1.68 |  |  |  | $114.12 |  |  |  |  |  |  | $25.59
Ferrite Bead | Analog Supply | DigiKey | 445-172886-1-ND | 1 | $0.10 | $0.10
MMBT2222AL | Click NPN Trans | DigiKey | MMBT2222ALT1GOSCT-ND | 1 | $0.13 | $0.13
BAS16J | Reset Circuit Bias | DigiKey | 1727-6169-1-ND | 1 | $0.18 | $0.18
LED 0603 | Indicator LEDs | DigiKey | 511-1588-1-ND | 3 | $0.44 | $1.32
MBR0520LT1 | 12V Diode | DigiKey | ‎MBR0520LT1GOSCT-ND‎ | 1 | $0.29 | $0.29
10u Ind | 12V Inductor | DigiKey | ‎490-10563-1-ND‎ | 1 | $0.42 | $0.42
220p 0603 Cap | 12V Stability Cap | DigiKey | 311-4111-1-ND | 1 | $0.10 | $0.10
0.1u Cap | Bypass Caps | DigiKey | 399-1100-1-ND | 9 | $0.10 | $0.90
10u Cap | LF Filtering | DigiKey | 311-2007-1-ND | 3 | $0.23 | $0.69
2.2u 0603 Cap | 12V Filtering | DigiKey | 399-7886-1-ND | 1 | $0.14 | $0.14
4.7u 0603 Cap | 12V Filtering | DigiKey | 399-3482-1-ND | 1 | $0.19 | $0.19
117k 0603 Res | 12V Bias Res | Mouser | 603-RT0603DRE07117KL | 1 | $0.13 | $0.13
51k 0603 Res | 12V SHDN Pullup | DigiKey | 749-1754-1-ND | 1 | $0.17 | $0.17
13.3k 0603 Res | 12V Bias Res | DigiKey | RMCF0603FT13K3CT-ND | 1 | $0.10 | $0.10
22 Res | USB Resistors | Digikey | A129668CT-ND | 2 | $0.10 | $0.20
330 Res | LED Resistor | DigiKey | P330HCT-ND | 7 | $0.10 | $0.70
10k Res | Pull Up Res | DigiKey | 311-10KGRCT-ND | 4 | $0.10 | $0.40
1k 0603 Res | Click Current Res | DigiKey | 311-1.0KGRCT-ND | 1 | $0.10 | $0.10
1M 0603 Res | Sensor Divider Res | DigiKey | 311-1.00MHRCT-ND | 4 | $0.10 | $0.40
 |  |  |  |  |  | $21.24

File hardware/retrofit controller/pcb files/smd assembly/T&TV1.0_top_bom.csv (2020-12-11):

Comment | Designator | Footprint | LCSC Part #
0.1u | S1 S2 C2 C4 C5 | C0603K
0.1u | C8 C9 | C0603
0.1u | C13 C15 C16 C17 | C0603K
1M | R10 R11 R12 R13 | R0603
1k | R16 | R0603
2.2u | C6 | C0603
3.3V | U3 | SOT23-5
4.7u | C7 | C0603
10k | R6 R14 R15 R17 | R0603
10u | C3 C10 C11 | C1206
13.3k | R2 | R0603
22 | R19 R20 | R0603
30Ω/1.8A | FB2 | 0603
51k | R1 | R0603
117k | R5 | R0603
220p | C1 | C0603
250mA/100V | D14 | SOD-323
330 | R3 R4 R7 R8 R9 R18 R21 | R0603
600mA/40V | Q1 | SOT23-3
1239AS-H-100M=P2 | L1 | IND_DFE252012C
ATSAMD21E18A | U5 | QFN32_5X5MC
LMR62014XMFE/NOPB | U1 | MF05A
MBR0520 | U4 | SOD-123
RED | D1 D2 D3 | LED-0603
TB6612FNG | U$1 | SSOP24

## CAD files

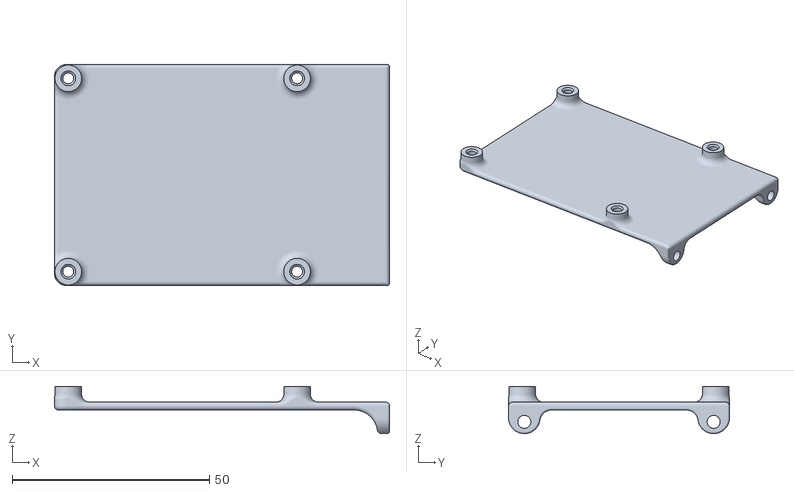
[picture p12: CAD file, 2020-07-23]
hardware/rpi mount/PiMount.stl
84.9 x 56.0 x 12.0

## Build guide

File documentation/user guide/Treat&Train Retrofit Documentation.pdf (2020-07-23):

University of Nebraska – Lincoln Department of Psychology
Center for Brain, Biology, and Behavior Dr. Jeffrey Stevens

Treat & Train Retrofit Documentation and User Guide 17 May 2020
V1.4
Overview
The PetSafe Treat & Train Manners Minder Remote Reward Dog Trainer is a commercial, at-home tool for performing operant conditioning with your dog. Using an RF remote control, the dispensation of treats can be controlled by the user based on the settings indicated by the switch interface on the top of the device.

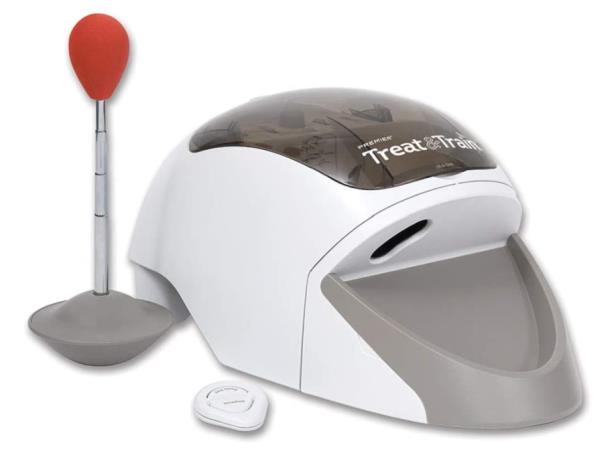
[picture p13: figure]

Figure 1 – Treat & Train Device

A main operation of the device is to train your dog to perform a “Down/Stay” command, which is facilitated by the dispensation of a pre-determined number of treats.

Treat & Train Operation
When the Treat & Train is operated in the single treat dispensation mode, meaning that a single treat is dispensed when the ‘Dispense’ button on the RF remote is clicked, it monitors two devices:
1. IR break sensor on the treat dispensing eyelet,
2. IR break sensor on an internal mirror locked to the rotation of the dispensing wheel.

There are two stop conditions for the dispensing wheel:
1. The eyelet break sensor is triggered,
2. The wheel performs a full rotation.

These two conditions are the main driving signals for operation of the device.

Retrofitted Circuit Description
The functionality of the Treat & Train was analyzed, and reverse engineered and reimplemented on a custom board, which allows for future expansion and software-based upgrades. The IR sensors that are used for the primary operation of the device are hooked up to resistor divider bridges to act as a voltmeter. The on-board motor driver interfaces to the main DC motor inside of the device. The motor output of the Treat & Train is hooked up to a transistor to detect when the main board is requesting a treat. The system voltage is boosted to 12V to drive the DC motor and the entire system operates off of the USB power input.

Prototype Board

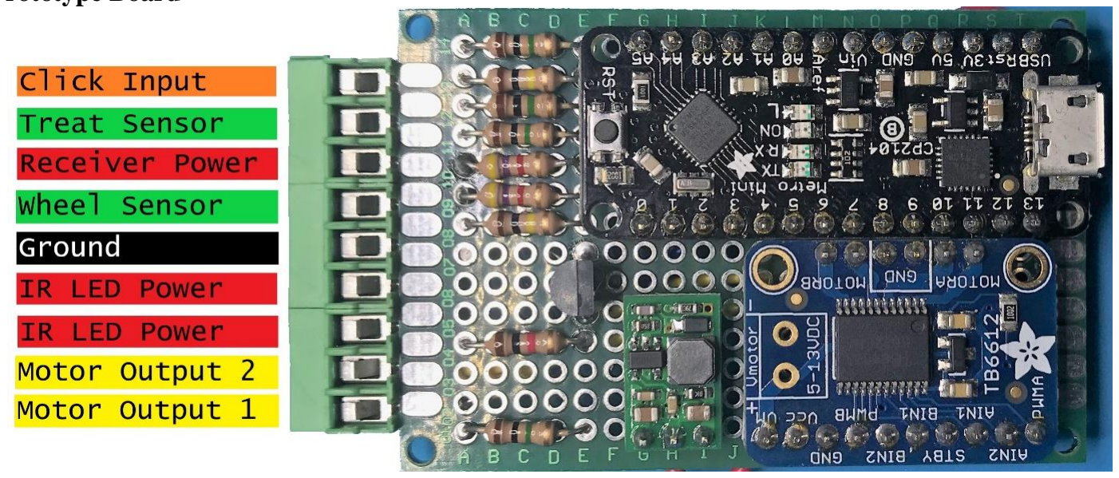
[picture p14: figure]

Figure 2 – Working Circuit on Protoboard including Pinout

Pin Name | Arduino Pin | Function | Description
Motor Output 2 | N/A | Output | Connected to negative motor pin
Motor Output 1 | N/A | Output | Connected to positive motor pin
IR LED Power | N/A | Output | 5V power supply for IR LEDs, current limited to 5mA
Ground | N/A | Input | Common ground pin
Wheel Sensor | A1 | Input | IR break sensor output from wheel sensor
Receiver Power | N/A | Output | 5V power supply for break sensors, current limited to 1mA
Treat Sensor | A3 | Input | IR break sensor from treat sensor
Click Input | 4 | Input | RF remote input for ‘Dispense’ button

The on-board motor driver is connected to the Adafruit Metro Mini, which is an equivalent design to the Arduino Uno. The outputs from the Metro Mini are defined below.

Pin Name | Arduino Pin | Description
BIN1 | 9 | First input for motor driver, invert from other input to drive motor in one direction or the other.
BIN2 | 8 | Second input for motor driver, invert from other input to drive motor in one direction or the other.
PWMB | 6 | PWM input that controls the speed of the motor, accepts values between 0-255. Default: 127

At this time, there is no working implementation using the wheel sensor.

When using the RF remote to trigger the system, the Treat & Train main board must first be plugged in before plugging in the retrofitted board.

Do not use anything other than a computer USB port for powering the system. The retrofitted board does not power the Treat & Train main board and the main device will still require four D cell batteries to operate.

Custom Printed Circuit Board
The custom board implements the functionality of the prior prototype board, with a fully integrated hardware solution.

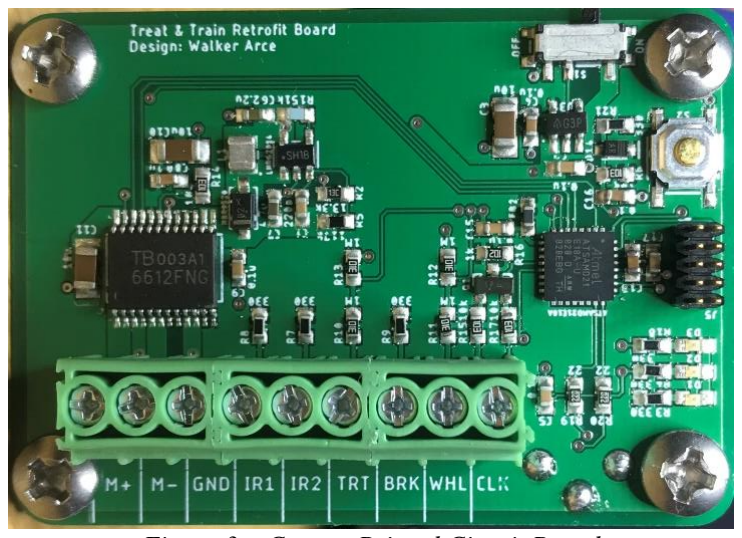
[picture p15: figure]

Figure 3 – Custom Printed Circuit Board

Pin Name | Arduino Pin | Function | Description
M+ | N/A | Output | Connected to positive motor pin
M- | N/A | Output | Connected to negative motor pin
GND | N/A | Input | Common ground pin
IR1 | N/A | Output | 3.3V power supply for IR LEDs, current limited to 5mA
IR2 | N/A | Output | 3.3V power supply for IR LEDs, current limited to 5mA
TRT | A1 | Input | IR break sensor from treat sensor
BRK | N/A | Output | 3.3V power supply for break sensors, current limited to 1mA
WHL | A3 | Input | IR break sensor output from wheel sensor
CLK | D8 | Input | RF remote input for ‘Dispense’ button
Pin Name | Arduino Pin | Description
AIN1 | D7 | First input for motor driver, invert from other input to drive motor in one direction or the other.
AIN2 | D6 | Second input for motor driver, invert from other input to drive motor in one direction or the other.
PWMA | D3 | PWM input that controls the speed of the motor, accepts values between 0-255. Default: 127

At this time, there is no working implementation using the wheel sensor.

When using the RF remote to trigger the system, the Treat & Train main board must first be plugged in before plugging in the retrofitted board.

Do not use anything other than a computer USB port for powering the system. The retrofitted board does not power the Treat & Train main board and the main device will still require four D cell batteries to operate. This board shows up as the “Sparkfun Qwiic Micro” when seen in the Arduino IDE.

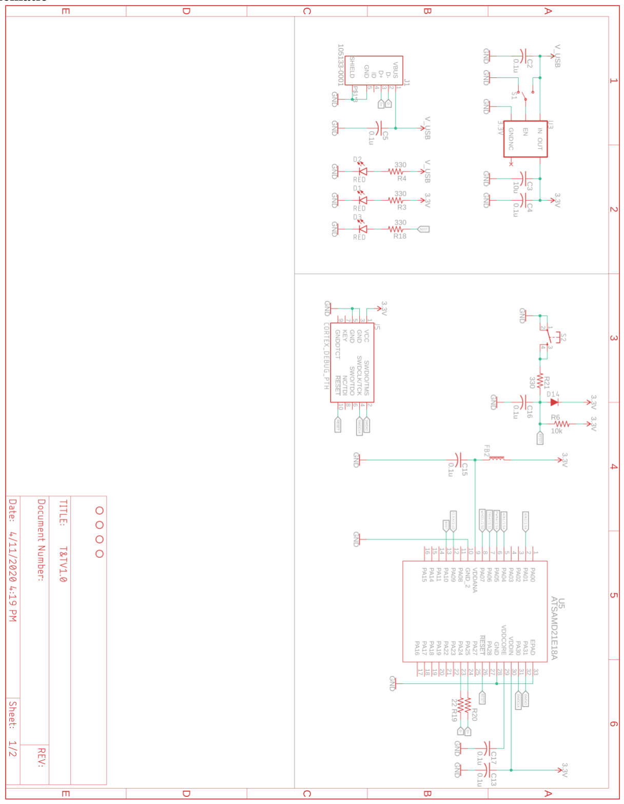
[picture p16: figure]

Schematic

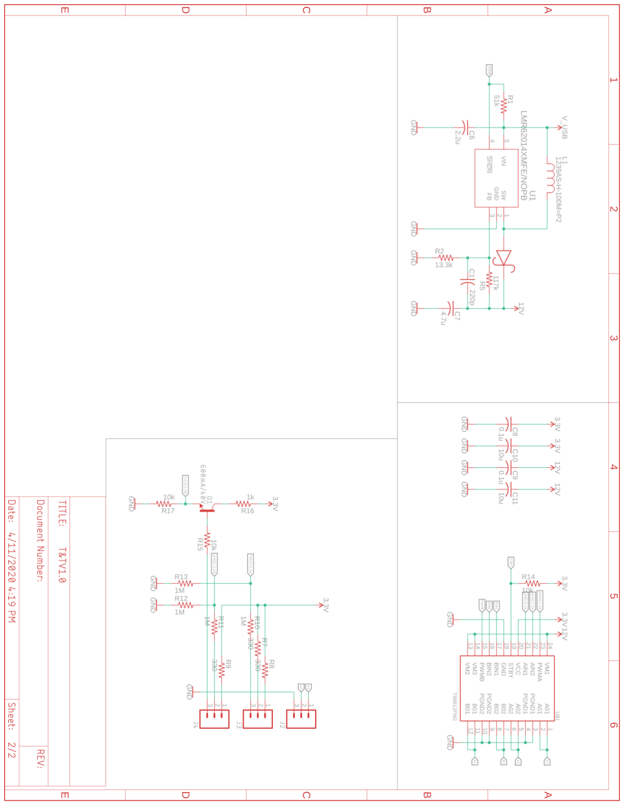
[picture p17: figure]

USB Protocol
The system operates using a defined USB protocol driven by byte codes. This can be easily expanded upon in the firmware by adding cases to the switch statement for the command byte. This is defined below.
Name | Value | Function
Start Byte | 67 (Dec), 0x43, ‘C’ | Signals the system to start listening for input
Command Byte | 1 byte | Command defined below
Data Byte | 1 byte | Defined based on commands
End Byte | 69 (Dec), 0x45, ‘E’ | Signals the system to stop listening for input

There are a few pre-defined commands for this version of the firmware, one of which is not accessible through USB input.

Command | Byte | Data | Function
Dispense | ‘D’ | 0-9 (ASCII) | Command to dispense treats, the number of treats is between 0 and 9 in ASCII.
Print | ‘P’ | 0 (ASCII) | Prints current value of sensors, data field is set to zero in ASCII
Update RF | ‘B’ | 0-9 (ASCII) | Updates the number of treats dispensed when using the RF remote.
Dispense | ‘A’ | 0-255 (ASCII) | Command to dispense treats, the number of treats is interpreted as the hex value of the ASCII char for data
Motor Update | ‘M’ | 0-255 (ASCII) | Updates the motor speed used when operating the dispenser in any mode
Wheel Test | ‘F’ | 0 (ASCII) | Performs the wheel test routine to verify operation of the device and sensors
RF Dispense | N/A | N/A | By clicking the ‘Dispense’ button on the RF remote, the system will dispense the defined number of treats. Default: 1 treat

Python Class Definition

class CanineDispenser
__init__(comport_name='/dev/ttyACM0', delay=1)
Parameters: comport_name – device name, defaults to Linux device name delay – period in seconds to delay to account for reset update_rf_amount(num_treats)
Parameters: num_treats – the number of treats to dispense, int [0, 9] Returns: 0 for success, 1 for failure, byte dispense_treats(num_treats)
Parameters: num_treats – the number of treats to dispense, int [0, 9] Returns: 0 for success, 1 for failure, byte dispense_treats_multi(num_treats)
Parameters: num_treats – the number of treats to dispense, int [0, 255] Returns: 0 for success, 1 for failure, byte change_motor_speed(motor_speed)
Parameters: motor_speed – new motor speed, int [0, 255]
Returns: 0 for success, 1 for failure, byte
debug_sensors()
Returns: output line of the dispenser for state of sensors, str wheel_test()
Returns: None. Outputs sensor information to command line disconnect()

list_comports()
Returns: list containing serial objects that are available, list read_dispenser_line(dispenser)
Parameters: dispenser – CanineDispenser object to operate on
Returns: string containing dispenser output, str dispenser_test(expected_dispensers)
Parameters: expected_dispensers – number of dispensers to connect to, int Returns: None. Outputs information to the command line dispenser_functionality_test(comport_name)
Parameters: comport_name – string representing COM port to connect to Returns: None. Outputs information to the command line

Interfacing Example
The retrofitted board can be interfaced using any modern system, but for this document Python 3.7 is used to interface to the system. A single library is needed, pySerial, which can be installed using Pip.

comports = list_comports()

dispensers = []

while expected_dispensers != 0:
try:
com_select = input("Select COM port from list above: ")
if int(com_select) < 0 or int(com_select) > len(comports) - 1:
print('Invalid input. Valid range is 0 to', len(comports) - 1)
else:
dispensers.append(CanineDispenser(comport_name=comports[int(com_select)].device)) expected_dispensers -= 1
except:
print('Invalid COM port selected, use numerals in range [0, 9]. Returning control.') return

while True:
command = input('Enter number of treats to dispense [0, 9] or "exit" to quit: ') try:
if command is 'exit':
for dispenser in dispensers:
dispenser.disconnect()
return
elif int(command) < 0 or int(command) > 9: print('Invalid input. Valid range is [0, 9].') else:
for dispenser in dispensers:
out = dispenser.dispense_treats(command)
if out == b'1':
print('Invalid command for', dispenser.comport.name) elif out == b'0':
print('Successful command for', dispenser.comport.name) except:
print('Invalid input. Only use numerals [0, 9] or type "exit". Returning control.') return

Notice below that the new Treat & Train shows up as USB Serial Device on COM31.

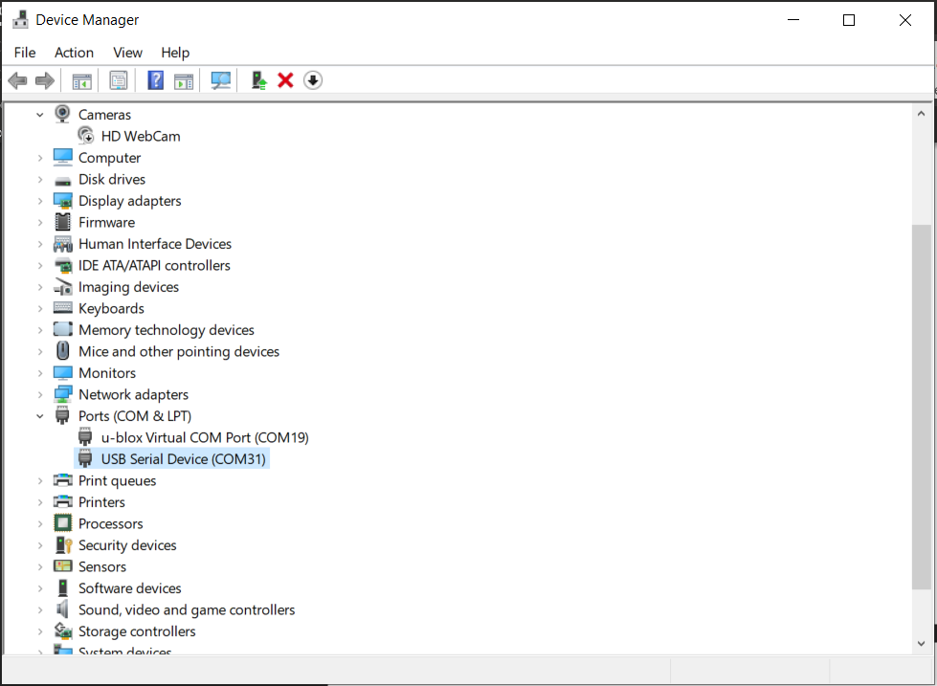
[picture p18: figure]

Raspberry Pi 4 as an Experiment Platform
The experiments on canine operant conditioning are run using a Python package called PsychoPy. It essentially acts as a development environment for psychology experiments and provides a variety of utilities for user interface development, trigger conditions, experiment logging, and so on. Our aim is to integrate this directly into a Raspberry Pi 4, to allow the entire setup to become a mobile testing unit. To do this, we will have a few requirements:
1. Wireless Access Point
a. The Raspberry Pi 4 should host its own WiFi access point (AP), which allows the experimenter to connect to the Pi and run experiments, download results, and interact with the main system.
2. Decoupled Interfaces
a. The screen the experimenter will use, and the screen used by the canine will be separate and require no extra hardware to achieve. By connecting to the Pi using SSH (Secure Shell), the command line can be exposed to run the experiments. The canine screen can be connected to the HDMI0 of the Pi and the SSH session can be started in a separate area.
3. Simple Setup
a. We want to make sure this is easy to setup and maintain. This means that we would want to use robust packages such as ‘pi-ap’ and SD card backups to easily restore the device and get new devices up and running easily.

There are two ways to setup a new Raspberry Pi to operate the canine dispenser:
1. Flash a new SD card with an image from the iso_images folder
a. Using a Raspberry Pi with a fresh installation of Raspbian Buster, there are built-in tools to achieve this. (https://www.raspberrypi.org/documentation/linux/filesystem/backup.md) “The SD Card Copier application, which can be found on the Accessories menu of the Raspberry Pi Desktop, will copy Raspbian from one card to another. To use it, you will need a USB SD card writer. To back up your existing Raspbian installation, put a blank SD card in your USB card writer and plug it into your Pi, and then launch SD Card Copier. In the ‘Copy From Device’ box, select the internal SD Card. This could have a number of different names and may have something like (/dev/mmcblk0) in its entry, but will usually be the first item in the list. Then select the USB card writer in the ‘Copy To Device’ box (where it will probably be the only device listed). Press ‘Start’. The copy, depending on the size of the SD card, can take ten or fifteen minutes, and when complete you should have a clone of your current installation on the new SD card. You can test it by putting the newly-copied card into the Pi’s SD card slot and booting it; it should boot and look exactly the same as your original installation, with all your data and applications intact.”
2. Follow the proceeding instructions to setup the Raspberry Pi manually.
a. Flash a new copy of Rasbian Buster onto a micro SD card and place an empty file named “ssh” onto the boot partition. There is no file extension.
b. Connect the Raspberry Pi to your local network using an Ethernet cable and power up the Pi. You can connect a monitor, keyboard, and mouse and use ifconfig to find the IP address of the Pi.
c. Using this IP address, go to PuTTY and type in this IP address and connect to the Pi. The default password for “pi” is “raspberry”.
d. Once in, the pi-ap software (https://github.com/f1linux/pi-ap) can be installed to create the access point. Note, the dog_operant repository does contain a copy of this, but the main repository will contain the most recent version.
e. The dog_operant (https://github.com/adaptive-decision-making-lab/dog_operant) repository can be cloned using the git clone command.
f. Run the command sudo apt-get update g. You will need to upgrade pip using
python3 -m pip install --upgrade pip
which will allow it to index some of the following packages.
h. Run the command
python3 -m pip install psychopy==3.2.4
which will install all the needed packages. Using the older version of PsychoPy will prevent a ‘Segmentation fault’ caused when rendering a new Window.
i. You may get an error saying that there is no package called ‘wx’, in which case you need to run the command
python3 -m pip install wxPython
j. If you want to run experiments, you will need to connect a screen to the Pi on HDMI0. An issue may present itself where no screen is presented when connected, which is caused by an incorrect /boot/config.txt file. To fix this do the following:
i. sudo nano /boot/config.txt
ii. Add the following to the file or uncomment from the file,
1. hdmi_force_hotplug=1
2. hdmi_drive=2
iii. If this does not fix the issue, add,
1. hdmi_safe=1
k. To run an experiment, use the following command
export DISPLAY=:0 ; python3 dog_operant/system_test.py
Note, this works from the command line, so run this when you are connected to an SSH session and with a screen connected to HDMI0 of the Pi and the experiment will display over HDMI0. Setting the DISPLAY variable to 0 will default it to the local display.
3. To transfer the results of the experiments, copy the contents of the data directory from the dog_operant directory. Use the following command structure:

scp -r user@ssh.example.com:/path/to/remote/source /path/to/local/destination

Raspberry Pi Interfacing and Passwords
The dispenser, when turned on, will create a WiFi access point called, “operant-canine-xx”, with “xx” being the number, i.e. “01”. By connecting to this, the Raspberry Pi can be accessed through SSH using a program called PuTTY. (https://www.chiark.greenend.org.uk/~sgtatham/putty/latest.html)
Local Address | Password
pi@192.168.0.1 | cb3stevens
pi@adml-stevens-01 | cb3stevens

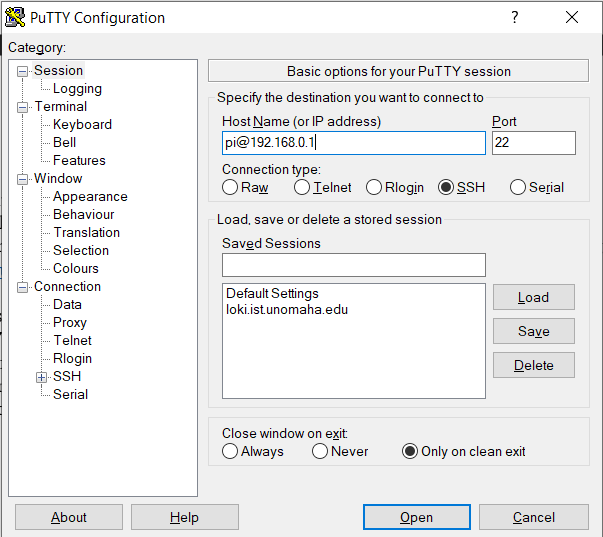
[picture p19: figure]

Bill of Materials
Printed Circuit Board Parts

Build Parts

Part | Description | Supplier | Part Number | Quantity | Price | Final Price
ATSAMD21E | Microcontroller | DigiKey | ATSAMD21E18A-MUTCT-ND | 1 | $2.92 | $ 2.92
TB6612FNG | Motor Driver | DigiKey | TB6612FNGC8ELCT-ND | 1 | $1.95 | $ 1.95
LMR6201 | 12V Boost | DigiKey | LMR62014XMFE/NOPBCT-ND | 1 | $1.64 | $ 1.64
AP2112K | 3.3V LDO | DigiKey | AP2112K-3.3TRG1DICT-ND | 1 | $0.49 | $ 0.49
Vertical USB | USB Connector | DigiKey | WM9734CT-ND | 1 | $1.11 | $ 1.11
Screw Terminal | Sensor Connectors | DigiKey | ED10562-ND | 3 | $1.03 | $ 3.09
Debug Header | Programming Header | DigiKey | 609-3712-ND | 1 | $0.69 | $ 0.69
SPST Switch | Reset Button | DigiKey | CKN12223-1-ND | 1 | $0.10 | $ 0.10
SPDT Switch | Power Switch | DigiKey | 401-2016-6-ND | 1 | $0.91 | $ 0.91
Stand Off | Board Mounting | DigiKey | 36-24434-ND | 4 | $0.42 | $ 1.68
Ferrite Bead | Analog Supply | DigiKey | 445-172886-1-ND | 1 | $0.10 | $ 0.10
MMBT2222AL | Click NPN Trans | DigiKey | MMBT2222ALT1GOSCT-ND | 1 | $0.13 | $ 0.13
BAS16J | Weather Sensor Diodes | DigiKey | 1727-6169-1-ND | 1 | $0.18 | $ 0.18
LED 0603 | Indicator LEDs | DigiKey | 511-1588-1-ND | 3 | $0.44 | $ 1.32
MBR0520LT1 | 12V Diode | DigiKey | MBR0520LT1GOSCT-ND | 1 | $0.29 | $ 0.29
10u Ind | 12V Inductor | DigiKey | 490-10563-1-ND | 1 | $0.42 | $ 0.42
220p 0603 Cap | 12V Stability Cap | DigiKey | 311-4111-1-ND | 1 | $0.10 | $ 0.10
0.1u Cap | Bypass Caps | DigiKey | 399-1100-1-ND | 9 | $0.10 | $ 0.90
10u Cap | LF Filtering | DigiKey | 311-2007-1-ND | 3 | $0.23 | $ 0.69
2.2u 0603 Cap | 12V Filtering | DigiKey | 399-7886-1-ND | 1 | $0.14 | $ 0.14
4.7u 0603 Cap | 12V Filtering | DigiKey | 399-3482-1-ND | 1 | $0.19 | $ 0.19
117k 0603 Res | 12V Bias Res | Mouser | 603-RT0603DRE07117KL | 1 | $0.13 | $ 0.13
51k 0603 Res | 12V SHDN Pullup | DigiKey | 749-1754-1-ND | 1 | $0.17 | $ 0.17
13.3k 0603 Res | 12V Bias Res | DigiKey | RMCF0603FT13K3CT-ND | 1 | $0.10 | $ 0.10
22 Res | USB Resistors | Digikey | A129668CT-ND | 2 | $0.10 | $ 0.20
330 Res | LED Resistor | DigiKey | P330HCT-ND | 7 | $0.10 | $ 0.70
10k Res | Pull Up Res | DigiKey | 311-10KGRCT-ND | 4 | $0.10 | $ 0.40
1k 0603 Res | Click Current Res | DigiKey | 311-1.0KGRCT-ND | 1 | $0.10 | $ 0.10
1M 0603 Res | Sensor Divider Res | DigiKey | 311-1.00MHRCT-ND | 4 | $0.10 | $ 0.40

Bill of Materials - Treat&Train Retrofit Board

Part | Supplier | Quantity | Price
Raspberry Pi 4 | Sparkfun | 1 | $ 59.95
16 GB SD Card | Amazon | 1 | $ 6.99
Power Supply | Sparkfun | 1 | $ 8.00
USB C Panel Mount Cord | Amazon | 1 | $ 8.99
HDMI Panel Mount | Amazon | 1 | $ 1.59
Micro HDMI to HDMI Cord | Amazon | 1 | $ 5.41
Micro USB to USB A Cord | Sparkfun | 1 | $ 1.95

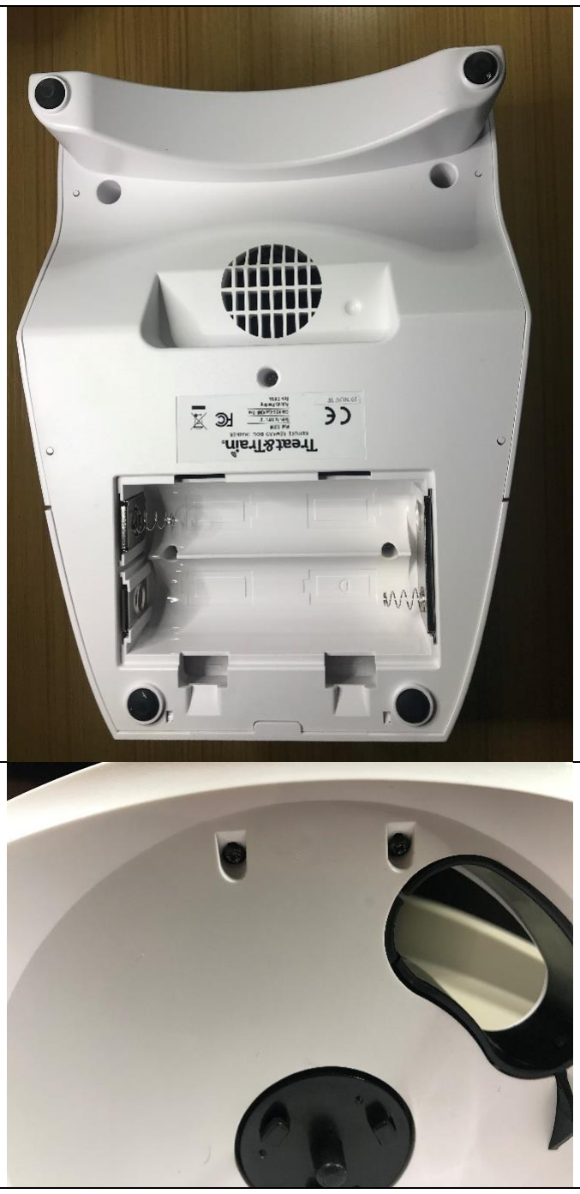
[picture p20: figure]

Build Instructions
1. Flip the Treat & Train over and remove the five screws holding the bottom plate on.
2. Next, flip the device over, open the treat reservoir and locate the two screws on the wheel face and remove them. Remove both this plate and the bottom plate, flipping over the device to expose the internal electronics.

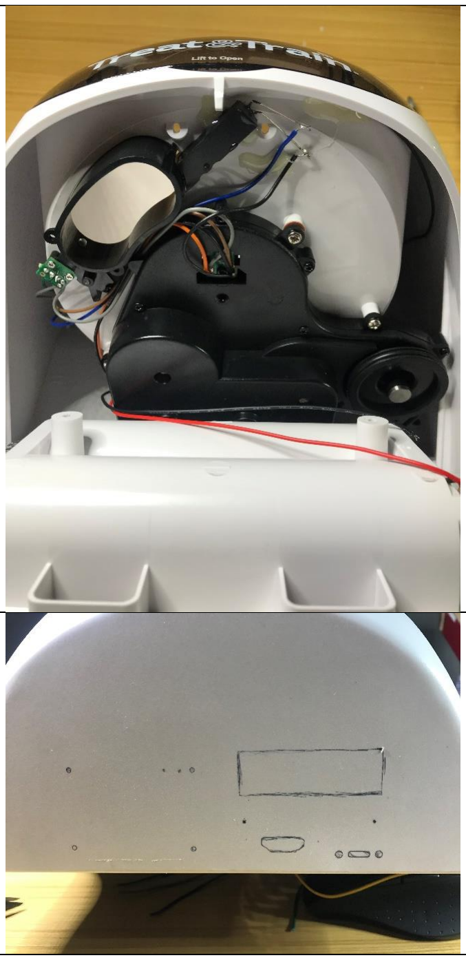
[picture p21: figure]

3. Observe the front exposed face and locate the black wire connected to the top IR receiver. This is marked in red. Cut it and solder on a new red wire approximately four inches in length. This is the output signal labeled ‘TRT’ on the custom board.
4. Flip the device around and mark on the back face where the new electronics will be exposed.

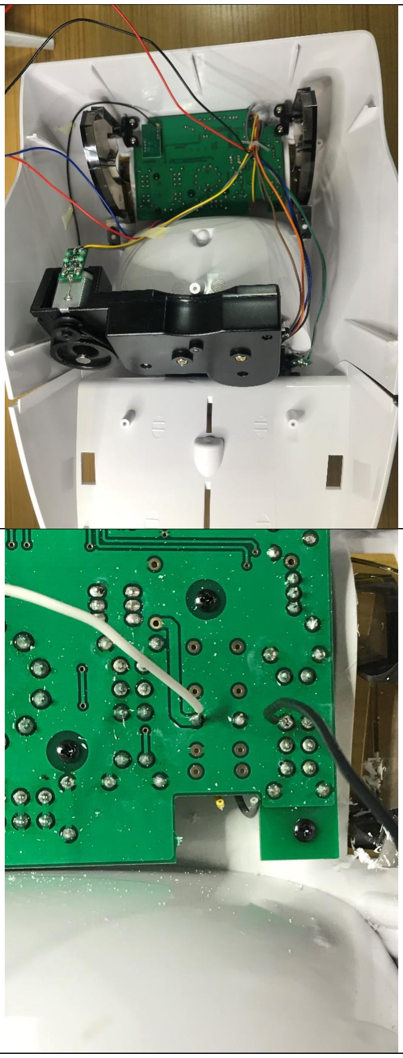
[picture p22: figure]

5. Now, observe the internal electronics of the stock device and notice the cord bundle on the top right of the device. Cut all of these except for the red and black power wires that go to the battery bank. Strip the ends of the cut wires and place them to the side.
6. Next, tack on two wires to the shown pads on the underside of the internal board. The white wire will be our ‘Click’ signal and the black will be the common ground of the stock electronics.

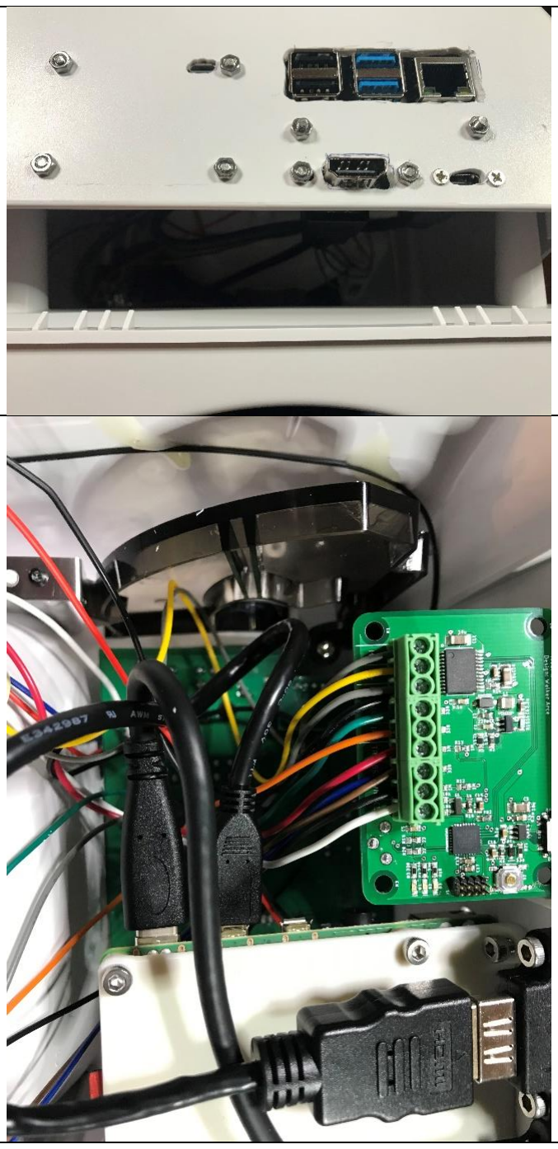
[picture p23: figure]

7. Bore out the marked ports on the back of the device and install the electronics using M3 screws. Eight will be required of the 12mm variety. Additionally, notice the teeth on the inner wall of the bottom plate. Clip these off using flush cutters as the installed electronics will get in the way of them.
8. Now, install the wires from the internals of the device to the custom board shown.

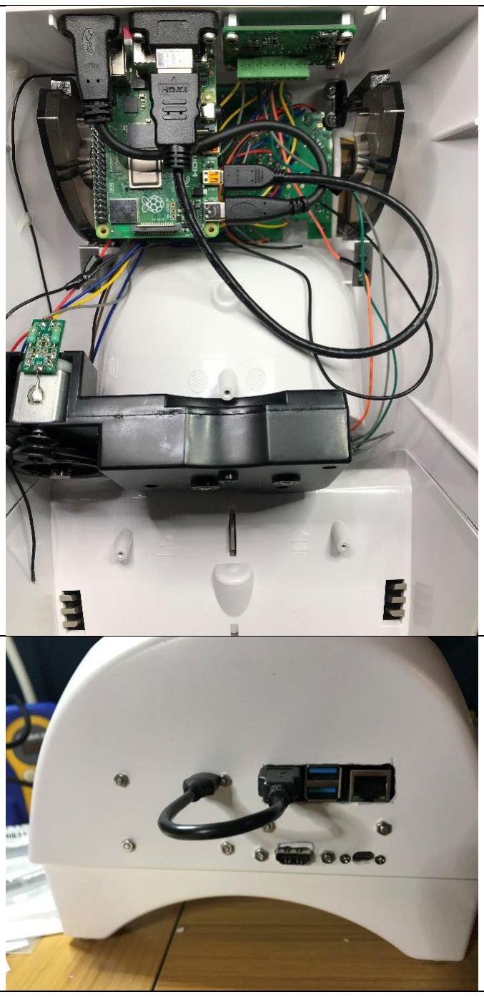
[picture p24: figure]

9. Note, for this build we used as custom a Raspberry Pi, right angle mounting plate. Now, connect the associated wires to Pi.
10. Screw the device back together and plug in the short USB cable from the Pi to the custom board.

Firmware
pins.h

#define MDRIVERA 7

#define MDRIVERB 6

#define MSPEED 3

#define CLICK 8

#define WHEEL_SENSOR A3

#define TREAT_SENSOR A1

TreatAndTrainDriverCustomBoard.ino

/*
* Treat & Train Custom Driver
* Author: Walker Arce, May 2020
*
* This program is used to drive the Treat & Train device for pellet dispensation.
* It operates using a simple USB command protocol and can also be driven by the use of the * accompanying RF remote.
*
* The current operation of the system is as follows:
* | 1. A command is sent over USB to dispense a pellet,
* | a. Drives wheel until pellet sensor is broken or wheel goes a full rotation.
* | 2. The button 'Dispense' is clicked on the RF remote
* | a. Drives wheel until pellet sensor is broken or wheel goes a full rotation.
*
* The motor can be driven at a variety of levels, for the second state of operation, it will be driven at half speed (6V DC).
*
* This initial version is meant to simply replicate functionality. The Treat & Train can be restored to original functionality
* by reconnecting the internal board and sensors.
*
* v0.3
* 12 May 2020
*/

#include "pins.h"

#define Serial | SerialUSB

#define SerialDebug | false

#define VOLTAGE_SCALE 3.3

#define ADC_PRECISION 4096.0

#define LOGIC_LOW | 0.09

//Voltage sensing variables
float Vout = 0.00;
float Vin = 0.00;
float R1 = 1000000.00; // resistance of R1 (1M) float R2 = 1000000.00; // resistance of R2 (1M)

//Peripheral sampling variables
float sampleVoltage = 0;
float wheelVoltage = 0;
float treatVoltage = 0;
int clickSignal = 0;

int clickCycles = 1;
int globalMotorSpeed = 127;

void setup()
{
Serial.begin(9600);
analogReadResolution(12); // Set analog input resolution to max, 12-bits initPins();
stopMotor();
//while(1){ debugSensors(); }
//moveMotor(125, true);
}

void loop()
{
//Listen for the RF remote
if (digitalRead(CLICK) == HIGH)
{
if(dispenseCommand(clickCycles, 127, false, false)) {
Serial.println("Successfully dispensed");
}

else
{
Serial.println("Error occurred"); }
while(digitalRead(CLICK) == HIGH) {} }
//Wait for USB input
while(Serial.available() > 0)
{
char command[4];
size_t bytesRead = Serial.readBytes(command, 4); //Check for 'C' being sent
if (command[0] == 67 && command[3] == 69)
{
switch(command[1])
{
//Check for 'D' being sent
//This dispenses the specified number of treats, give or take. case 68:
if (dispenseCommand(command[2], globalMotorSpeed, false, true)) {
Serial.print(0x00, HEX);
}
else
{
Serial.print(0x01, HEX);
}
break;
//Check for 'P' being sent
//This prints out the current state of the internal sensors. case 80:
debugSensors();
break;
//Check for 'B' being sent
//This updates the number of treats dispensed when RF remote is clicked case 66:
clickCycles = command[2] - 0x30;
Serial.print(0x00, HEX);
break;
//Check for 'A' being sent
//This is meant to be used when more than nine treats are expected to be dispensed //Does not convert ASCII character to decimal
case 65:
if (dispenseCommand(command[2], globalMotorSpeed, false, false))
{
Serial.print(0x00, HEX);
}
else
{
Serial.print(0x01, HEX);
}
break;
//Check for 'M' being sent
//This allows the changing of the global motor speed //Not recommended to be used
case 77:
globalMotorSpeed = command[2];
Serial.print(0x00, HEX);
break;
//Command not recognized
default:
Serial.print(0x01, HEX);
}
}
else
{
Serial.print(0x01, HEX);
}
}
}

void testWheel()
{
int motorSpeed = 0;
while(motorSpeed < globalMotorSpeed)
{
moveMotor(motorSpeed++, true);
wheelVoltage = getVoltage(WHEEL_SENSOR, 10); wheelVoltage = roundFloat(wheelVoltage, 1);

treatVoltage = getVoltage(TREAT_SENSOR, 10);

treatVoltage = roundFloat(treatVoltage, 1);

Serial.print("Wheel Voltage: "); Serial.print(wheelVoltage);
Serial.print("V | Treat Voltage: ");
Serial.print(treatVoltage); Serial.print("V");
Serial.print(" | Speed: ");
Serial.print(motorSpeed);
Serial.println();
delay(200);
}
stopMotor();
}

void debugSensors()
{
moveMotor(127, true);

wheelVoltage = getVoltage(WHEEL_SENSOR, 10); wheelVoltage = roundFloat(wheelVoltage, 1);

treatVoltage = getVoltage(TREAT_SENSOR, 10); treatVoltage = roundFloat(treatVoltage, 1);

Serial.print("Wheel Voltage: "); Serial.print(wheelVoltage);
Serial.print("V | Treat Voltage: ");
Serial.print(treatVoltage); Serial.print("V");
Serial.println();
delay(200);
}

bool dispenseCommand(int cycles, int motorSpeed, bool motorDir, bool isASCII) {
sampleVoltage = getVoltage(TREAT_SENSOR, 10);
sampleVoltage = roundFloat(sampleVoltage, 1);

int treatSamples = cycles;
if (isASCII) { treatSamples = cycles - 0x30; } int wheelSamples = treatSamples * 3; moveMotor(motorSpeed, motorDir);

while (treatSamples > 0)
{
treatVoltage = getVoltage(TREAT_SENSOR, 10); treatVoltage = roundFloat(treatVoltage, 1);

if (treatVoltage < sampleVoltage)
{
treatSamples--;
while (treatVoltage < sampleVoltage)
{
treatVoltage = getVoltage(TREAT_SENSOR, 10); treatVoltage = roundFloat(treatVoltage, 1); }
}
}
stopMotor();
return true;
}

//Source: https://stackoverflow.com/questions/1343890/how-do-i-restrict-a-float-value-to-only-two-places-after-the-decimal-point-in-c
float roundFloat(float raw, int precision)
{
return floorf(raw * (10 * precision)) / 10;
}
//Source: https://create.arduino.cc/projecthub/next-tech-lab/voltmeter-using-arduino-00e7d1 float getVoltage(int pin, int samples)
{
int val = getAverageReading(pin, samples);
Vout = (val * VOLTAGE_SCALE) / ADC_PRECISION; // formula for calculating voltage out i.e. V+, here 5.00 Vin = Vout / (R2/(R1+R2)); // formula for calculating voltage in i.e. GND
if (Vin < LOGIC_LOW)//condition
{
Vin=0.00;
}
return Vin;
}

int getAverageReading(int pin, int numReadings) {
int adcReading = 0;
for (int i = 0; i < numReadings; i++)
{
adcReading += analogRead(pin);
}
adcReading /= numReadings; return adcReading;
}

void moveMotor(int motorSpeed, bool motorDir) {
//Set motor speed before driving motor analogWrite(MSPEED, motorSpeed);
//If true, then drive it clockwise
if (motorDir)
{
digitalWrite(MDRIVERA, HIGH); digitalWrite(MDRIVERB, LOW);
}
//If false, then drive it counter-clockwise else
{
digitalWrite(MDRIVERA, LOW); digitalWrite(MDRIVERB, HIGH); }
}

void stopMotor()
{
analogWrite(MSPEED, 0);
digitalWrite(MDRIVERA, LOW); digitalWrite(MDRIVERB, LOW); }

void initPins()
{
//Initialize inputs
pinMode(WHEEL_SENSOR, INPUT); pinMode(TREAT_SENSOR, INPUT); pinMode(CLICK, INPUT);

//Initialize outputs
pinMode(MDRIVERA, OUTPUT); pinMode(MDRIVERB, OUTPUT); pinMode(MSPEED, OUTPUT);
}

dispenser_utilities.py

"""dispenser_utilities.py

This script creates a serial interface to the retrofitted Treat & Train device developed for Dr. Jeffrey Stevens' canine operant conditioning studies. The member methods comply with the USB protocol developed to interact with its internal state machine
and encapsulates a comport definition and a configurable delay period.

Supported device operations include (replace X with relevant value):
Dispense treats in [0, 9] range: | CDXE
Dispense treats in [0, 255] range: | CAXE
Update the RF remote dispensation amount in range [0, 9]: | CBXE
Update motor speed in range [0, 255]: | CMXE
Debug sensors: | CP0E
Wheel test routine: | CF0E

Note: The value placed in X will be represented in ASCII, so for the 'D' command it will be valid in ASCII range
[0, 9], in which case the device will convert the value passed from ASCII to decimal. In the case of the 'A'
command, it treats the ASCII value as the number of treats and does not convert the value to decimal.

Supports version 0.4 of the dispenser firmware.

Author: | Walker Arce
Date: | 05/17/2020
Version: | 0.3
"""

import serial import serial.tools.list_ports import time

class CanineDispenser:
"""A simple class definition to interact with the canine treat dispenser.

self.comport - pyserial USB port object used to communicate with the device. self.delay - period in seconds to wait before sending command to allow for reset. """
def __init__(self, comport_name='/dev/ttyACM0', delay=1):
"""
Parameters
:param comport_name: str
The name of the USB port to connect to, i.e. '/dev/ttyACM0' or 'COM31' :param delay: int or float
The period in seconds to wait before sending command to allow for reset """
try:
self.comport = serial.Serial(comport_name, baudrate=9600, timeout=None) self.delay = delay
except serial.SerialException:
print('Failed to open serial port, double check port and try again.') print('Port: ' + comport_name)

def update_rf_amount(self, num_treats):
"""Sends a command to the dispenser to update the number of treats dispensed when using the RF remote. Parameters
:param num_treats: int
The number of treats in range [0, 9] to dispense
:return: byte
0 for success, 1 for failure
"""
if num_treats < 0 or num_treats > 9:
print('Number of treats must be within range [0, 9], please retry.')
return
if self.comport.isOpen():
command = 'CB'.encode('ascii') + str(num_treats).encode('ascii') + 'E'.encode('ascii') time.sleep(self.delay)
self.comport.write(command)
return self.comport.read(1)

def dispense_treats(self, num_treats):
"""Sends command to dispense treats in range [0, 9] Parameters
:param num_treats: int
The number of treats in range [0, 9] to dispense :return: byte
0 for success, 1 for failure
"""
if int(num_treats) < 0 or int(num_treats) > 9:
print('Number of treats must be within range [0, 9], please retry. ' 'Use dispense_treats_multi to dispense more treats.')
return
if self.comport.isOpen():
command = 'CD'.encode('ascii') + str(num_treats).encode('ascii') + 'E'.encode('ascii') time.sleep(self.delay)
self.comport.write(command)
else:
print('No open comport on this object.') return
return self.comport.read(1)

def dispense_treats_multi(self, num_treats):
"""Sends command to dispense a greater amount of treats, in range [0, 255] Parameters
:param num_treats: int
The number of treats to dispense in range [0, 255]
:return: byte
0 for success, 1 for failure
"""
if int(num_treats) < 0 or int(num_treats) > 255:
print('Number of treats must be within range [0, 255], please retry.')
return
if self.comport.isOpen():
command = 'CA'.encode('ascii') + chr(num_treats).encode('ascii') + 'E'.encode('ascii') time.sleep(self.delay)
self.comport.write(command)
return self.comport.read(1)

def change_motor_speed(self, motor_speed):

"""Sends command to update the motor speed with provided value in range [0, 255]
Note: Increasing the motor speed beyond 127 (default) is not recommended for expected use case. Parameters
:param motor_speed: int
Speed of the motor in range [0, 255] or [0V, 12V] equivalent
:return: byte
0 for success, 1 for failure
"""
if motor_speed < 0 or motor_speed > 255:
print('Motor speed must be within valid range [0, 255], please retry.')
return
if self.comport.isOpen():
command = 'CM'.encode('ascii') + chr(motor_speed).encode('ascii') + 'E'.encode('ascii') time.sleep(self.delay)
self.comport.write(command)
return self.comport.read(1)

def debug_sensors(self):
"""Sends command to get the current state of the sensors, used for debugging sensor issues :return: str
String representing the current value of the sensors
"""
if self.comport.isOpen():
self.comport.write('CP0E'.encode('ascii'))
return read_dispenser_line(self)

def wheel_test(self):
"""Sends command to run the wheel test procedure
Try breaking the eyelet sensor to verify operation or updating the motor speed to change the max speed :return: None
Loop is terminated by the dispenser sending a '0' for successful completion
"""
if self.comport.isOpen():
self.comport.write('CF0E'.encode('ascii'))
wheel_out = ""
while wheel_out != b'0':
wheel_out = read_dispenser_line(self) if wheel_out[-3:] != '127': print(wheel_out)
elif wheel_out[-3:] == '127': print(wheel_out)
wheel_out = self.comport.read(1)

def disconnect(self):
"""Disconnects the internal comport object. :return: none
"""
self.comport.close()

def list_comports():
"""Wrapper utility to show exposed COM ports.
:return: list
List consisting of serial object representing the available COM ports """
comports = serial.tools.list_ports.comports()
print([comport.device for comport in comports])
return comports

def read_dispenser_line(dispenser):
"""Wrapper function on serial.readline() function to handle Arduino Serial.println(). Use in loop to handle continuous output.
Source: https://stackoverflow.com/questions/24074914/python-to-arduino-serial-read-write
:param dispenser: CanineDispenser
Pass a dispenser object with an open comport
:return: str
Trimmed Arduino output string
"""
line_out = str(dispenser.comport.readline()) return line_out[2:][:-5]

def dispenser_test(expected_dispensers):
"""This function is to be used to test multiple dispensers for basic functionality Parameters
:param expected_dispensers: int
The number of dispensers to be connected to
:return: None
Used to break while loop, returns None value """

comports = list_comports()

dispensers = []

while expected_dispensers != 0:
try:
com_select = input("Select COM port from list above: ")
if int(com_select) < 0 or int(com_select) > len(comports) - 1:
print('Invalid input. Valid range is 0 to', len(comports) - 1)
else:
dispensers.append(CanineDispenser(comport_name=comports[int(com_select)].device)) expected_dispensers -= 1
except:
print('Invalid COM port selected, use numerals in range [0, 9]. Returning control.') return

while True:
command = input('Enter number of treats to dispense [0, 9] or "exit" to quit: ') try:
if command is 'exit':
for dispenser in dispensers:
dispenser.disconnect()
return
elif int(command) < 0 or int(command) > 9: print('Invalid input. Valid range is [0, 9].') else:
for dispenser in dispensers:
out = dispenser.dispense_treats(command)
if out == b'1':
print('Invalid command for', dispenser.comport.name) elif out == b'0':
print('Successful command for', dispenser.comport.name) except:
print('Invalid input. Only use numerals [0, 9] or type "exit". Returning control.') return

def dispenser_functionality_test(comport_name):
"""Sends all commands that return a byte return code. Parameters
:param comport_name: str
Name of the COM port, i.e. '/dev/ttyACM0' or 'COM31' :return: None
Prints state of the commands to command line
"""
dispenser = CanineDispenser(comport_name=comport_name) D_out = dispenser.dispense_treats(1)
A_out = dispenser.dispense_treats_multi(1)
M_out = dispenser.change_motor_speed(127)
RF_out = dispenser.update_rf_amount(1)

if D_out == b'0' and A_out == b'0' and M_out == b'0' and RF_out == b'0':
print('D: ', D_out, '\nA: ', A_out, '\nM: ', M_out, '\nRF: ', RF_out, '\nDispenser operating successfully.')
else:
print('D: ', D_out, '\nA: ', A_out, '\nM: ', M_out, '\nRF: ', RF_out, '\nDispenser not operating correctly.')

Document Revision History
Revision, Name, and Date | Revision Description
V0.1, Walker Arce, 21 March 2020 | First draft creation date for Treat & Train retrofitted circuit.
V1.0, Walker Arce, 27 April 2020 | Added documentation on custom board
V1.1, Walker Arce, 28 April 2020 | Added documentation on updated software
V1.2, Walker Arce, 12 May 2020 | Added docs on new commands and Raspberry Pi
V1.3, Walker Arce, 16 May 2020 | Added build instructions and bills of material
V1.4, Walker Arce, 17 May 2020 | Added Python source, updated interfacing, and commands

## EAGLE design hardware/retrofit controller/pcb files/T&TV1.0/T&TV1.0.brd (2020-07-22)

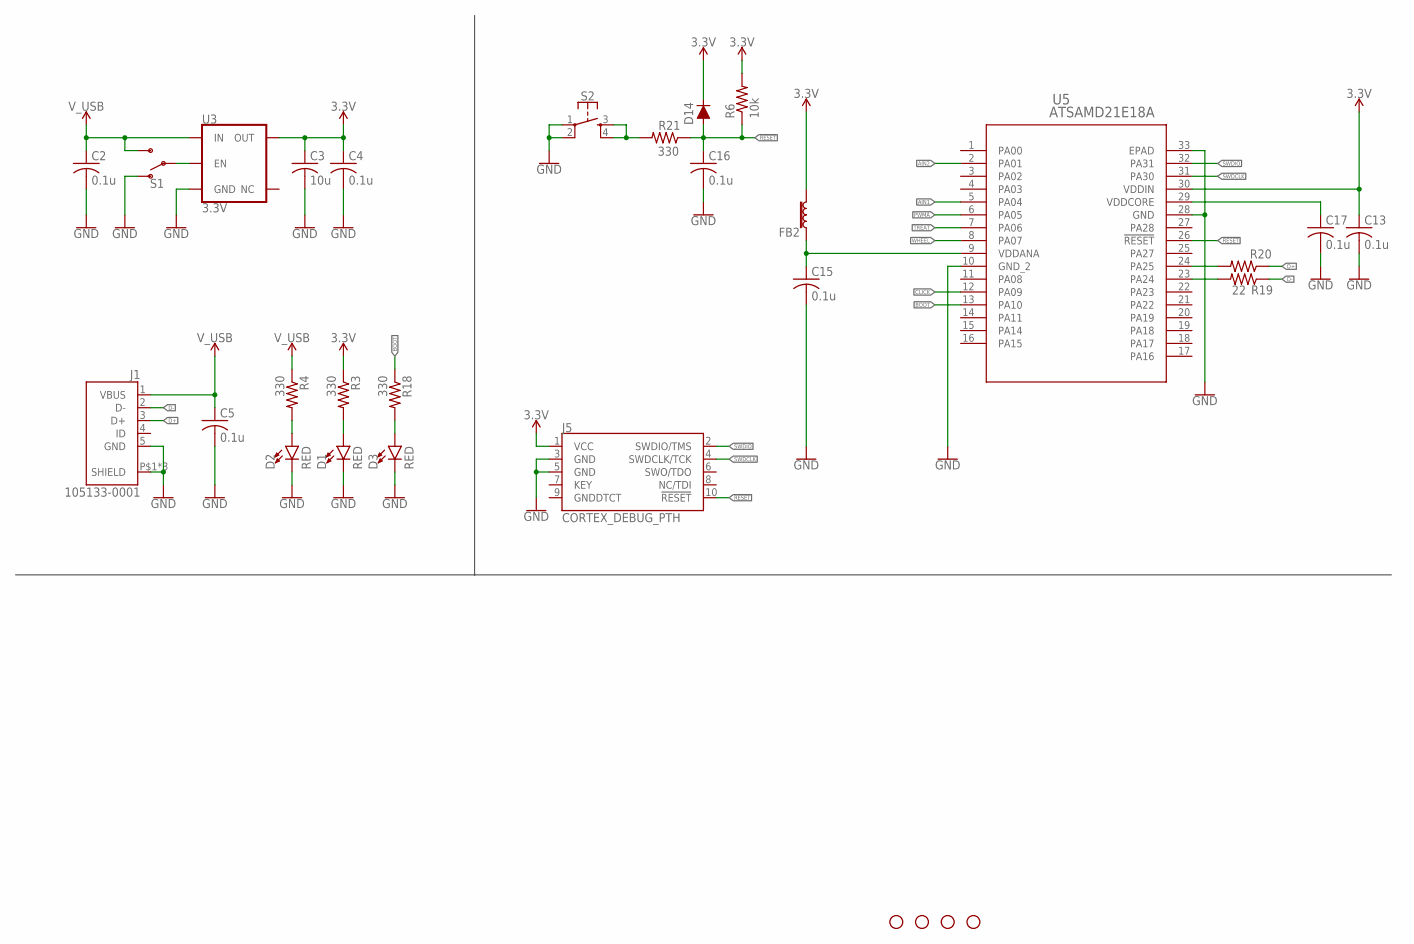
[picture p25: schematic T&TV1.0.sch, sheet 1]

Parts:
C2, C4, C5, C13, C15, C16, C17: 0.1u; C0603K
C3: 10u; C1206
D1, D2, D3: RED; LED-0603
D14: 250mA/100V; SOD-323
FB2: 30Ω/1.8A; 0603
H1, H2, H3, H4: STAND-OFF
J1: 105133-0001; MOLEX_105133-0001
J5: CORTEX_DEBUG_PTH; 2X5-PTH-1.27MM
R3, R4, R18, R21: 330; R0603
R6: 10k; R0603
R19, R20: 22; R0603
S1: SWITCH-SPDT-SMD-RIGHT-ANGLE; SWITCH_SPST_SMD_A
S2: MOMENTARY-SWITCH-SPST-2-SMD-5.2MM; TACTILE_SWITCH_SMD_5.2MM
U3: 3.3V; SOT23-5
U5: ATSAMD21E18A; QFN32_5X5MC

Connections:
3.3V: C3.1, C4.1, C13.1, D14.C, FB2.2, J5.1 (VCC), R3.1, R6.2, U3.5 (OUT), U5.30 (VDDIN); also elsewhere on the board
!RESET: C16.1, D14.A, J5.10 (!RESET), R6.1, R21.1, U5.26 (!RESET)
AIN1: U5.5 (PA04); also elsewhere on the board
AIN2: U5.2 (PA01); also elsewhere on the board
BOOT: R18.1, U5.13 (PA10)
CLICK: U5.12 (PA09); also elsewhere on the board
D+: J1.3 (D+), R20.1
D-: J1.2 (D-), R19.1
GND: C2.2, C3.2, C4.2, C5.2, C13.2, C15.2, C16.2, C17.2, D1.C, D2.C, D3.C, J1.5 (GND), J1.P$1 (SHIELD), J1.P$2 (SHIELD), J1.P$3 (SHIELD), J5.3 (GND), J5.5 (GND), S1.1 (O), S2.1, S2.2, U3.2 (GND), U5.10 (GND_2), U5.28 (GND), U5.33 (EPAD); also elsewhere on the board
unnamed: D1.A, R3.2
unnamed: C15.1, FB2.1, U5.9 (VDDANA)
unnamed: C17.1, U5.29 (VDDCORE)
unnamed: D2.A, R4.2
unnamed: D3.A, R18.2
unnamed: R20.2, U5.24 (PA25)
unnamed: R19.2, U5.23 (PA24)
unnamed: R21.2, S2.3, S2.4
unnamed: S1.2, U3.3 (EN)
PWMA: U5.6 (PA05); also elsewhere on the board
SWDCLK: J5.4 (SWDCLK/TCK), U5.31 (PA30)
SWDIO: J5.2 (SWDIO/TMS), U5.32 (PA31)
TREAT: U5.7 (PA06); also elsewhere on the board
V_USB: C2.1, C5.1, J1.1 (VBUS), R4.1, S1.3 (S), U3.1 (IN); also elsewhere on the board
WHEEL: U5.8 (PA07); also elsewhere on the board

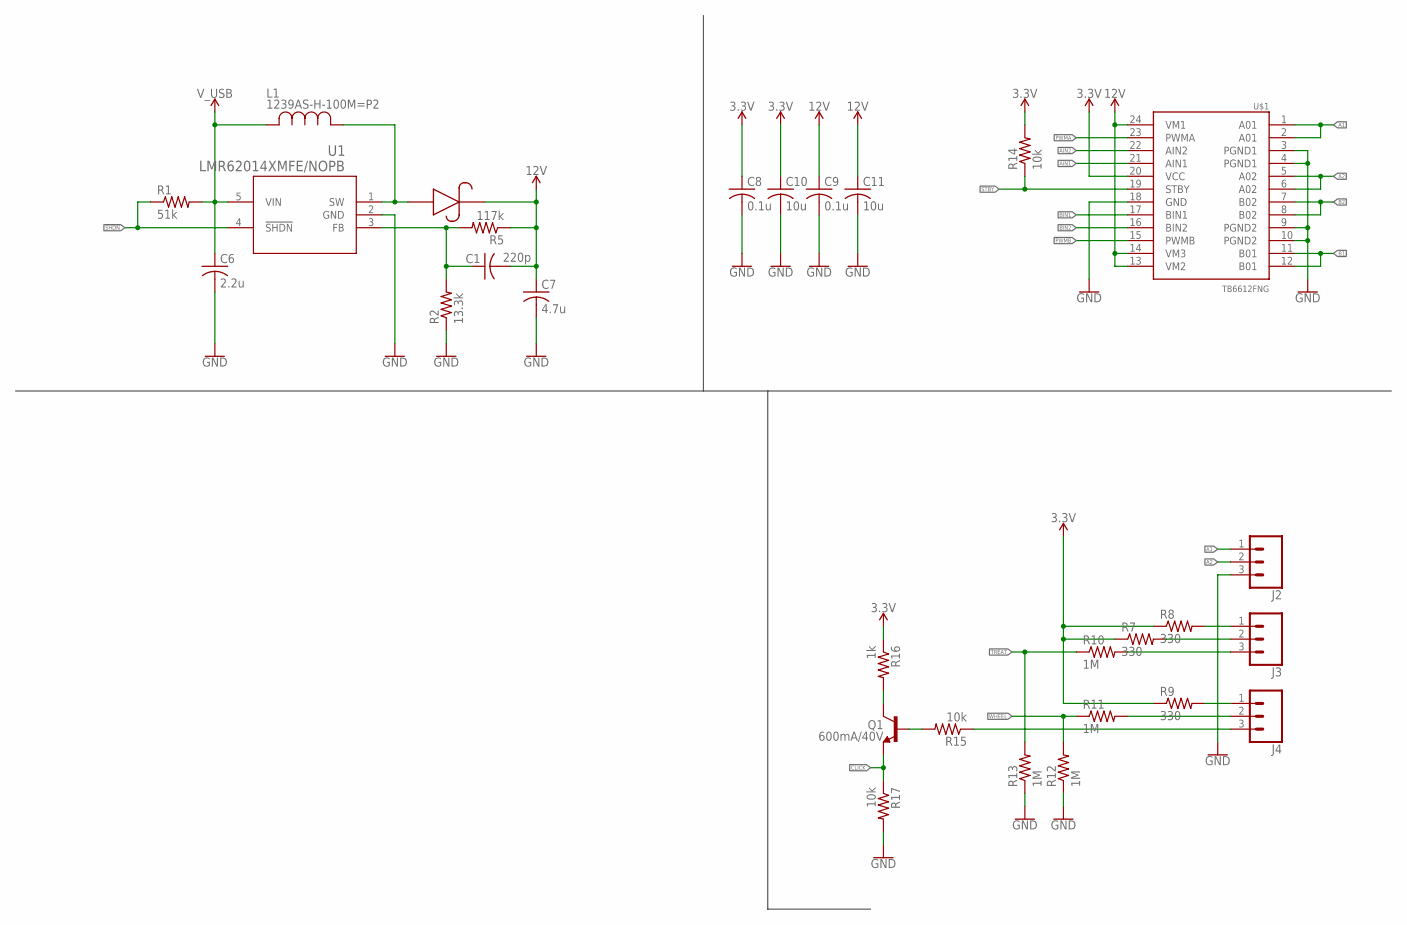
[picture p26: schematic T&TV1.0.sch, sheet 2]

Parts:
C1: 220p; C0603
C6: 2.2u; C0603
C7: 4.7u; C0603
C8, C9: 0.1u; C0603
C10, C11: 10u; C1206
J2, J3, J4: CONN_03SCREW-NS; SCREWTERMINAL-3.5MM-3-NS
L1: 1239AS-H-100M=P2; IND_DFE252012C
Q1: 600mA/40V; SOT23-3
R1: 51k; R0603
R2: 13.3k; R0603
R5: 117k; R0603
R7, R8, R9: 330; R0603
R10, R11, R12, R13: 1M; R0603
R14, R15, R17: 10k; R0603
R16: 1k; R0603
U1: LMR62014XMFE/NOPB; MF05A
U4: MBR0520; SOD-123
U$1: TB6612FNG; SSOP24

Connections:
3.3V: C8.1, C10.1, R7.1, R8.1, R9.1, R14.2, R16.1, U$1.20 (VCC); also elsewhere on the board
12V: C1.2, C7.1, C9.1, C11.1, R5.1, U4.2, U$1.13 (VM2), U$1.14 (VM3), U$1.24 (VM1)
!SHDN: R1.1, U1.4 (!SHDN)
A1: J2.1, U$1.1 (A01), U$1.2 (A01)
A2: J2.2, U$1.5 (A02), U$1.6 (A02)
AIN1: U$1.21 (AIN1); also elsewhere on the board
AIN2: U$1.22 (AIN2); also elsewhere on the board
B1: U$1.11 (B01), U$1.12 (B01)
B2: U$1.7 (B02), U$1.8 (B02)
BIN1: U$1.17 (BIN1)
BIN2: U$1.16 (BIN2)
CLICK: Q1.2 (E), R17.1; also elsewhere on the board
GND: C6.2, C7.2, C8.2, C9.2, C10.2, C11.2, J2.3, R2.1, R12.1, R13.1, R17.2, U1.2 (GND), U$1.3 (PGND1), U$1.4 (PGND1), U$1.9 (PGND2), U$1.10 (PGND2), U$1.18 (GND); also elsewhere on the board
unnamed: Q1.1 (B), R15.2
unnamed: L1.1, U1.1 (SW), U4.1
unnamed: J3.1, R8.2
unnamed: J3.2, R7.2
unnamed: C1.1, R2.2, R5.2, U1.3 (FB)
unnamed: J4.1, R9.2
unnamed: J3.3, R10.2
unnamed: Q1.3 (C), R16.2
unnamed: J4.2, R11.2
unnamed: J4.3, R15.1
PWMA: U$1.23 (PWMA); also elsewhere on the board
PWMB: U$1.15 (PWMB)
STBY: R14.1, U$1.19 (STBY)
TREAT: R10.1, R13.2; also elsewhere on the board
V_USB: C6.1, L1.2, R1.2, U1.5 (VIN); also elsewhere on the board
WHEEL: R11.1, R12.2; also elsewhere on the board

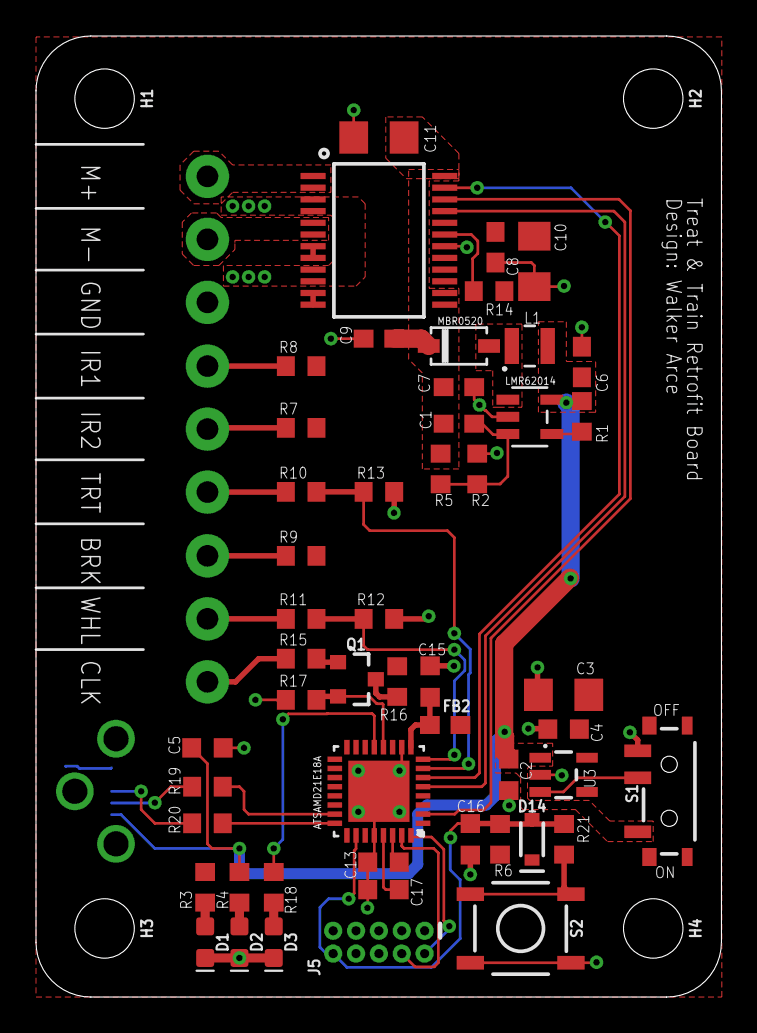
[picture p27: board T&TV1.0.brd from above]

Board: 2 copper layers, 38.1 x 53.4 mm, 59 parts (1 on the bottom side), 41 nets.

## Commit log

2020-07-23 Updated files
    Added python driver
    Added both Arduino firmwares
    Added gerbers and renders
    [PiMount.stl, T&TV1.0.brd, T&TV1.0.sch]
2020-07-28 Updated file structure for repo
    [T&TV1.0.brd, T&TV1.0.sch, TTBOM.xlsx]
2020-07-31 Updated a line in the BOM descriptions
    [TTBOM.xlsx]
2020-09-29 Rename and revise data and R script
    - Rename files
    - Rename trial column of data file
    - Add preamble to R script
    - Clean up R script
    - Create README file
    [arce_stevens_2020_data.csv]
2020-12-11 Added SMT assembly files
    Generated by: https://github.com/oxullo/jlcpcb-eagle
    [T&TV1.0_top_bom.csv, T&TV1.0_top_cpl.csv]

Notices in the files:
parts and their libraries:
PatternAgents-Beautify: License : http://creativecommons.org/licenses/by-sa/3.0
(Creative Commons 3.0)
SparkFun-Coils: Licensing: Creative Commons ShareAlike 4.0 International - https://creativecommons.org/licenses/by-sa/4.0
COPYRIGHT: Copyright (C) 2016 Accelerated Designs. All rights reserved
